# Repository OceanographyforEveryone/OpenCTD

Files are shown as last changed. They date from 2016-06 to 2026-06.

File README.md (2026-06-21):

# OpenCTD Rev8 is here!

**The ocean belongs to everyone.** The tools to study the ocean should be accessible to anyone with the curiosity and motivation to pursue that inquiry. Build your own [research-quality oceanographic instrument](https://tos.org/oceanography/article/the-openctd-a-low-cost-open-source-ctd-for-collecting-baseline-oceanographic-data-in-coastal-waters) and let's explore the ocean, together. 

# OpenCTD: Oceanography for Everyone

The CTD is an oveanographic instrument that measures salinity, temperature, and depth. By measuring these
characteristics, scientists can begin to unlock ocean patterns hidden beneath the sea's surface.

CTDs come in a variety of shapes, sizes, and applications. Most oceanographic research vessels have a CTD connected to a rosette platform, which houses other instruments and collects water samples in parallel with real-time data. CTDs are also commonly attached to fixed moorings, autonomous underwater vehicles (AUVs), remote-operated vehicles (ROVs), and even to marine animals.

Unfortunately, commercial CTDs are expensive. The most affordable models cost several thousand dollars. For near-shore oceanographic research on the relatively shallow continental shelf, this cost can be prohibitive. This
effectively excludes formal researchers from low and middle income countries, and small island states. Even in high-income countries, formal researchers at teaching institutions or at early career stages may also find themselves priced out of ocean research. Informal researchers such as citizen oceanographers, educators, conservation and management practitioners and students of all levels face severe challenges accessing expensive scientific instruments. 

**You don’t need to ask for permission to understand your world.**

By building your own instruments to study and understand the natural world, you are expanding the circle of knowledge production. A scientist who can make their own instruments is not beholden to the cycles of funding and access that constrain formal, institutional inquiry. A researcher who can build and repair their own equipment is not dependent on the whims of academic sentiment to decide what is and is not worthy of study. A community leader who has the tools to create their own data does not have to wait for institutions to take notice
of an emerging crisis before taking action. 

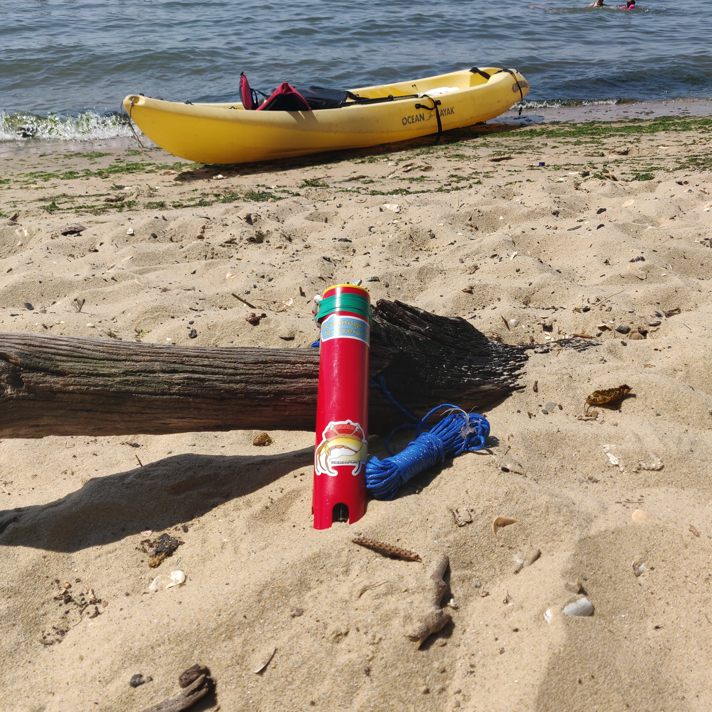
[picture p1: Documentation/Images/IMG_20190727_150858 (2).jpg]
The OpenCTD


### Build Your Own CTD

The OpenCTD is a low-cost, open-source CTD designed for budget-restricted
scientists, educators, and researchers working in nearshore coastal ecosystems.
In these waterways, entire research projects can be conducted for less than the
cost of a commercial CTD. OpenCTD was developed by a core team of marine
ecologists in collaboration with a community of scientists, engineers, makers,
and conservation practitioners from around the world. It is assembled from
components commonly available at large hardware stores or through major online
retailers. An Arduino-based microcontroller controls an array of sensors sealed
within a PVC pipe. Power is provided by a standard 3.7V lithium polymer battery
and data are stored in a tab-delimited text file accessed via SD card.  All
OpenCTD software is released open source with no restrictions on use. 

The OpenCTD built by the end-user, providing both access to
the tools of oceanography as well as the skills to maintain, repair, and
replace OpenCTDs. For scientists working in remote settings, the repairability
of the OpenCTD is intended to prevent equipment failures from spiraling into
project failures. For educators seeking novel, in-depth, hands-on STEM
experience for advanced students, the process of building an OpenCTD offers an
introduction to coding, 3D-printing, hardware prototyping, and electronics.
Construction of an OpenCTD can provide a practical foundation for courses in
oceanography and marine or environmental science. 

# Visit [Oceanography for Everyone](http://oceanographyforeveryone.com/) to learn more, inquire about workshops, or purchase OpenCTD kits!

### Publications

Thaler, A., S.K. Sturdivant, R.Y. Neches, and J.J. Levenson. 2024. [The OpenCTD: A low-cost, open-source CTD for collecting baseline oceanographic data in coastal waters](https://tos.org/oceanography/article/the-openctd-a-low-cost-open-source-ctd-for-collecting-baseline-oceanographic-data-in-coastal-waters#citation). Oceanography 37(2):167–173, https://doi.org/10.5670/oceanog.2024.602.

### Core Resources

The [OpenCTD Construction and
Operation](https://github.com/OceanographyforEveryone/OpenCTD/tree/main/Documentation)
manual provides a comprehensive, step-by-step guide to building your own
OpenCTD, with a standard construction pathway as well as numerous alternatives
depending on parts availability and technical skills. A shorter manual covering just the calibration process is also available. 

The OpenCTD [core software](https://github.com/OceanographyforEveryone/OpenCTD/tree/main/Software) is designed
to be used with an M0-style Arduino microcontroller, for which we recommend the
[Adafruit Adalogger Feather M0](https://www.adafruit.com/product/2796). 

You can find all the Arduino libraries as described in the manual, as well as
software for calibrating the conductivity sensors in
[Support](https://github.com/OceanographyforEveryone/OpenCTD/tree/main/Software/Support).

Hardware file for both 3D printable components and the control unit PBC can be found in [Hardware](https://github.com/OceanographyforEveryone/OpenCTD/tree/main/Hardware)

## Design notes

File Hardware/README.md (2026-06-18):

# OpenCTD Hardware 

This directory contains hardware files for building the OpenCTD Rev8. The [3D printable shapefiles](https://github.com/OceanographyforEveryone/OpenCTD/tree/main/Hardware/3DPrints) include the PowerSquid protective chassis, the sensor baseplate, and the router jigs and other accessories. The [printed circuit boards](https://github.com/OceanographyforEveryone/OpenCTD/tree/main/Hardware/PCB) include the KiCad and Gerber files for the OpenCTD Rev8 Control Board and the Oceanography for Everyone Custom Pressure Sensor breakout board. 

If you've been lucky enough to recieve Andrew's business card, [Benchtester](https://github.com/OceanographyforEveryone/OpenCTD/tree/main/Hardware/Benchtester) includes instructions for building a working test board for OpenCTD components, though, please note, the Benchtester was designed for the OpenCTD Rev7. 

### Electronics

The OpenCTD is controlled by an [Adalogger Feather M0](https://www.adafruit.com/product/2796) microcontroller development board.

Instructions on how to upload OpenCTD firmware to the microcontroller board can
be found in [Documentation](https://github.com/OceanographyforEveryone/OpenCTD/tree/main/Documentation). General instructions and
learning resources about the Adalogger Feather M0 board itself can be found in the [Adafruit Learning
Guide](https://learn.adafruit.com/adafruit-feather-m0-adalogger/).

The OpenCTD electronics can be assembled using a breadboard, or using a custom PCB. The custom PCB is designed using [KiCad](https://www.kicad.org/), and can be ordered in small batches from many PCB fabrication services around the world using the files located in the [PCB](https://github.com/OceanographyforEveryone/OpenCTD/tree/main/Hardware/PCB) directory.

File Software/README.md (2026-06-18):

# OpenCTD Software

This directory contains software for using the OpenCTD. There are three types of
software here: firmware, which runs on the OpenCTD itself; support software, which includes the require Arduino libraries as well as software for calibrating the conductivity sensor; and analysis
software, which is used to process data files copied from the OpenCTD to
another device (such as a personal computer) for analysis.

### Support Notes

Users may encounter the following issue: ["Code doesn't compile due to problem in RTCLib. Happens for both OpenCTD_mo.ino and RTC_Reset.ino"](https://github.com/OceanographyforEveryone/OpenCTD/issues/37) which can be solved by installing the library [Adafruit_BusIO](https://www.arduino.cc/reference/en/libraries/adafruit-busio/)

### Firmware

The OpenCTD is controlled by an [Adalogger Feather
M0](https://www.adafruit.com/product/2796) microcontroller development board.
Instructions on how to upload OpenCTD firmware to the microcontroller board can
be found in the [Documentation](https://github.com/OceanographyforEveryone/OpenCTD/tree/main/Documentation). General instructions and
learning resources about the Adalogger Feather M0 board itself can be found in
the [Adafruit Learning
Guide](https://learn.adafruit.com/adafruit-feather-m0-adalogger/).

[OpenCTD_m0_Rev8](https://github.com/OceanographyforEveryone/OpenCTD/tree/main/Software/Firmware/OpenCTD_m0_Rev8): This is the core software
for the OpenCTD. The file `OpenCTD_m0_Rev8.ino` contains the firmware
used in normal deployment of the OpenCTD instrument.

### Support
[Calibration](https://github.com/OceanographyforEveryone/OpenCTD/tree/main/Software/Support/Serial_for_EC_Calibration_m0): The calibration software which allows users to calibrate the Atlas Scientific EZO conductivity sensor.

[RTC Reset](https://github.com/OceanographyforEveryone/OpenCTD/tree/main/Software/Support/RTC_Reset): A small program to help you reset the real-time clock if it falls out of sync. 

[Arduino Libraries](https://github.com/OceanographyforEveryone/OpenCTD/tree/main/Software/Support/Arduino%20Libraries): Four Arduino Libraries required to run the OpenCTD, in downloadable ZIP files. 

### Analysis

OpenCTD writes data
to its microSD card in a generic CSV format that is compatible with many
different tools. In the [Analysis](https://github.com/OceanographyforEveryone/OpenCTD/tree/main/Software/Analysis) directory, you will find a few
examples of how to import and process data from the OpenCTD using different
software packages. Please use the software that best suits your own needs.

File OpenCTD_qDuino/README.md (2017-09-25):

OpenCTD Introduction and Build Guide
=======

*__Updated 9/25/2017__*

### 1.0 Overview

**Conductivity, temperature, and depth (CTD).**  These three measurements allow scientists to unlock ocean patterns hidden beneath the sea's surface. The ocean is not uniform, it its filled with swirling eddies, temperature boundaries, layers of high and low salinity, changing densities, and other physical characteristics invisible to an observer floating upon its surface. To reveal these patterns oceanographers employ the CTD--an oceanographic instrument that, at its core, measures temperature, salinity, and depth for a water column. The CTD is the workhorse of oceanographic research. 

CTDs are expensive, and that expense can is a barrier-to-entry for formal and informal researchers with limited budgets, scientists from developing nations, citizen oceanographers, and students of all levels interested in learning more about their local coasts and waterways. 

The OpenCTD is a low-cost, open-source CTD suitable for both educators and researchers. The platform is built using reasonably accessible parts and is powered by an Arduino-based microcontroller. Source codes and building instructions are freely available. The device, sufficiently accurate for scientific research, can be constructed for approximately $300, and is effective to 100 meters depth.

Why 100 meters? For many coastal regions, 100 meters depth covers the majority of the ocean that is accessible by small boat and generally the average depth of the outer continental shelf. The OpenCTD is targeted to people working in this niche, where entire research projects can be conducted for less than the cost of a commercial CTD. The OpenCTD is scalable and someone with the inclination and expertise can adapt an OpenCTD to operate in deeper waters.

*__If you build an OpenCTD please let the [team at Oceanography For Everyone](http://oceanographyforeveryone.com/#meetAnchor) know. We love to keep up with the community of people building and using these devices. During your build session, or while using an OpenCTD or other [Oceanography for Everyone](http://oceanographyforeveryone.com/) tools, please consider tweeting using the [#HackTheOcean](https://twitter.com/hashtag/HackTheOcean?src=hash) hashtag so the community can follow your efforts!__*

#### 1.1 Skills Needed

Building an OpenCTD requires some basic soldering and coding knowledge but it is also a great opportunity to learn those skills. With an hour or two of practice, you can develop the soldering skills needed to build an OpenCTD. [This descriptive, illustrative comic from Mighty Ohm](http://mightyohm.com/files/soldercomic/FullSolderComic_EN.pdf) presents soldering fundamentals in an accesible and approachable format.

Andrew has used this [MightyOhn Geiger Counter Kit](http://mightyohm.com/blog/products/geiger-counter/) and this [Mega Menorah 9000 Soldering Kit](http://shop.evilmadscientist.com/productsmenu/756) to teach soldering and basic electronic principles to students from ages 10 to 65. 

Arduino is a relatively intuitive coding environment, but it can still seem daunting to first-time users. Practically, we have already created the code you will need to run the OpenCTD, but it is extremely beneficial, particularly for end users, to understand what the software is doing. The book [Environmental Monitoring with Arduino: Building Simple Devices to Collect Data About the World Around Us](http://amzn.to/2xB15Xi) is short, easy to understand, and will provide you with some ideas for expanding your inventory of open-source environmental sensors. 

### 2.0 Project Status

The OpenCTD is stable on the Qduino Mini platform with comprehensive build instructions provided and a growing user community. We have validated the OpenCTD against commercial CTDs and are confident in the quality of the data. Users around the world are building and testing their own units and helping with instrument validation.  

#### 2.1 Field Trials

As we test and refine the design of the OpenCTD, critical field trials with essential data for assessing the quality, accuracy, and durability of the device are archived in the [Field_Trials](https://github.com/OceanographyforEveryone/OpenCTD/tree/master/Field_Trials) repository.

+ **_Lake Superior, R/V Blue Heron_:** Initial field trials were completed in October of 2015 and analysis of the data from the first several casts confirms the accuracy of OpenCTD at it was cast against a commercial CTD. Additionaly, OpenCTD was successfully deployed to a depth of 140 meters. All data and field notes from the first Field Trial can be found in the [Blue Heron 15-11](https://github.com/OceanographyforEveryone/OpenCTD/tree/master/Field_Trials/Blue_Heron_2015-11) repository.

+ **_Gloucester Point, VA, Hurricane Hermine_:** Hurricane Hermine is a tropical cyclone that passed over our field site in coastal Virginia on September 4, 2016. To test the longevity of the batteries and the durability of the OpenCTD during long term deployments, Andrew placed two units in our Test Ditch (a tidally influence drainage ditch connected to the Mobjack Bay estuary), where they remained for 74 hours. Notes and data files can be found in the [HermineDeployment_9-2016](https://github.com/OceanographyforEveryone/OpenCTD/tree/master/Field_Trials/HermineDeployment_9-2016) respository.

### 3.0 Bill of Materials

We try to source as many parts as possible from accesible distibutors. **_NOTE: As Amazon is in the process of phasing out its aStore program, the Parts Depot is no longer being maintained. Please consult the below list for the most recent part recommendations._** Many components can also be purchased directly through the supplier, found on AliExpress, or sourced through auction sites for significantly less. Quality across suppliers for most parts has been generally consistent, though we have noticed a defect rate of about 10% with the sealed temperature sensors. 

**Please be aware: Part availability varies from month to month, and some components may become permanently unavailble or listed under a new manufacturer and product name. We do our best to keep the bill of material up to date, If you find any discrepancies, please email us.**

**Recommended Components**

Part	| Suplier	| Price	| Link	
---|---|---|---
Qduino Mini |	Sparkfun/Amazon	| $29.95	| https://www.sparkfun.com/products/13614	/ http://amzn.to/2wS8YUp
SD Card Reader Module	|  Amazon	| $5.66	| http://amzn.to/2jXSNnv 	
3.7V 2000mAh LiPo	| Amazon	| $14.98	| http://amzn.to/2y3nDRQ						
Conductivity K 1.0 Kit |	Atlas Scientific  |	$195.71	| https://www.atlas-scientific.com/product_pages/kits/ec_k1_0_kit.html	
DS18B20 Temperature Sensor | Amazon | $9.88 |	http://amzn.to/2yoBUo6				
MS5803-14BA	|	Mouser	| $22.85	| http://www.mouser.com/ProductDetail/Measurement-Specialties/MS580314BA01-00
SOIC to DIP Adapter	|	Sparkfun	| $2.95	| https://www.sparkfun.com/products/13655
0.1uF Capacitor	| Amazon	| $4.79	| http://amzn.to/2humBn9
10k Ohm Resistor	|	Amazon	| $4.19	| http://amzn.to/2yoCjqC	
4.7kOhm Resistor | Amazon	| $6.16	| http://amzn.to/2fMfmHe					
Hook-up wire	|	Amazon	| $22.00	| http://amzn.to/2hu54eJ	
Heat shrink tubing |	Amazon	| $5.99	|http://amzn.to/2wRQtPO	
2" Gripper Plug | Amazon | $9.41 | http://amzn.to/2jWVjdz

**Alternate Components**

Part	| Suplier	| Price	| Link	
---|---|---|---
MicroSD Card Read Module	|  Amazon	| $9.49	| http://amzn.to/2y4nSvS
Pressure Sensor Breakout - MS5803-14BA | SparkFun | $59.95 | https://www.sparkfun.com/products/12909
3" Gripper Plug | Amazon | $4.99 | http://amzn.to/2wS9qlC

**Some parts, such as resistors and capacitors, are very cheap but hard to source individually. We have tried to find the smallest lots that aren't excessively overpriced, but you may have better luck finding cheaper options, especially "intro to electronics"-type kits, which include many standard resistors and capacitors in small lots.** 

Additional components, like a pre-fabricated [pressure sensor module](https://www.sparkfun.com/products/12909), [LiPo batteries](https://www.sparkfun.com/products/8483), [SMD boards](https://www.sparkfun.com/products/13655), and the [qDuino Mini](https://www.sparkfun.com/products/13614) can be found at Sparkfun. The MS5803-14BA pressure sensor previously needed to be special ordered from a parts supplier, but [SparkFun](https://www.sparkfun.com/products/12909) has a (much more expensive) commercial 14-bar unit using the same sensor. 

Servoflo sells the raw, calibrated pressure sensor in both [14Bar](http://www.servoflo.com/download-archive/data-sheets/220-calibrated-digital-sensor-modules/614-ms5803-14ba) and [30Bar](http://www.servoflo.com/download-archive/data-sheets/220-calibrated-digital-sensor-modules/613-ms5803-30ba) modules. These are surface mounted sensors and require significant soldering skills to mount properly. Detailed descriptions of the differeces and benefits between the two pressure sensors is discussed in section 5.2. Mouser now sells individual MS5803-14BA sensor modules for a reasonable cost.

PVC pipe can be found at most home supply stores. If you want to get fancy, a [clear acrylic tube](http://amzn.to/2njFhqw) can add some flare to your build. Though the first OpenCTDs were built using 3" PVC pipe, we now recommend using 2" pipe for a more durable, compact device.

#### 3.1 Tools
- wire cutter
- wire stripper
- soldering iron
- solder tip cleaner
- helping hands soldering station
- epoxy gun
- needle-nosed pliers
- multimeter
- utility knife
- hot glue gun
- heat gun
- saw
- drill
- 1" bit (for holes in PVC)
- laptop
- micro-USB cable
- coffee maker (because coffee)

#### 3.2 Consumables
- sand paper
- Hysol E90-FL epoxy
- venturi mixing nozzles for epoxy
- solder
- desoldering braid
- electical tape
- hot glue
- mineral oil
- calibration standard for conductivity
- coffee

#### 3.3 3D printed parts
Several useful parts that will significantly improve the build process are 3D printable: [3D Printer Files](https://github.com/OceanographyforEveryone/OpenCTD/tree/master/3D_Printer_Files). While 3D printing allows rapid fabricating of small custom parts for very low cost, we recognize that access to a 3D printer is not universal. The OpenCTD can be entirely constructed without 3D printed parts. The sensor plate can be fabricated from cardboard if necessary (its purpose is to hold the sensors in place while the expoxy cures, once the epoxy is set, the plate serves no further function). The wire jig helps keep everything organized but is not necessary. The Jaunty CTD Cap is funny, but not particularly useful. If you would like to build an OpenCTD but do not have access to a 3D printer, please contact either Andrew or Russell and we will print the parts for you. If you're on [Thingiverse](https://www.thingiverse.com/), please Like, Collect, or Make our designs to help boost our profile in the 3D-printing community. 

+ [OpenCTD sensor template](https://www.thingiverse.com/thing:1641934)
+ [OpenCTD hardware frame and wire guide](https://www.thingiverse.com/thing:2500591)
+ [Jaunty Red Cap for the OpenCTD](https://www.thingiverse.com/thing:2470929)

#### 3.4 Required Arduino Libraries
+ Included with Arduino IDE:
  - [**SPI.**](https://www.arduino.cc/en/Reference/SPI) Serial Peripheral Interface for communicating with a standard SD card reader.
  - [**SoftwareSerial.**](https://www.arduino.cc/en/Reference/SoftwareSerial) For communicating with serial devices like the conductivity circuit.
  - [**Wire.**](https://www.arduino.cc/en/Reference/Wire) For communicating with I2C devices like the pressure sensor. 
+ Need to download and install ([How to install Arduino libraries](https://www.arduino.cc/en/Guide/Libraries)):
  + [**SD.**](https://www.arduino.cc/en/Reference/SD) For reading and writing to a standard SD card reader.
  + [**SparkFun_MS5803_I2C.**](https://github.com/sparkfun/SparkFun_MS5803-14BA_Breakout_Arduino_Library/tree/V_1.1.0) For the MS5803 14 Bar pressure sensor (*__Note__: if you decide to use a different pressure sensor, you will need to update this library*)
  + [**Dallas Temperature Control.**](https://milesburton.com/Dallas_Temperature_Control_Library) Allows you to communicate with the DS18B20 thermistor. 
  + [**OneWire.**](http://www.pjrc.com/teensy/td_libs_OneWire.html) For controlling the Dallas 1-wire family of devices. 

#### 3.5 Other Useful Software

+ [**Qduino.h and Qduino fuelGauge**](https://github.com/sparkfun/Arduino_Boards/tree/master/sparkfun/avr/libraries/Qduino) allows you to measure the charge on you battery. 
+ [**simple_serial_for_EC_calibration**](https://github.com/OceanographyforEveryone/OpenCTD/tree/master/Support_Code/simple_serial_for_EC_calibration) is a basic serial monitor program to help you calibrate the conductivity probe. 
+ [**TempProbeTester**](https://github.com/OceanographyforEveryone/OpenCTD/tree/master/Support_Code/TempProbeTester) allows you to test up to 26 temperature probes simultaneously and is useful for quality control and temperature calibrations. 
+ [**MS5803_14_test**](https://github.com/OceanographyforEveryone/OpenCTD/tree/master/Support_Code/MS5803_14_test) For testing the pressure sensor prior to installation. 

### 4.0 Arduino Qduino Pinouts

- **SD Card Reader:** CS (D4), SCK (D15), MOSI (D16), MISO (D14*)
- **Pressure Sensor:** SDA (D2), SCL (D3)
- **Temperature Sensors:** Data (D6)
- **Conductivity Circuit:** TX (D8), RX (D9)

\*older Qduinos may have this labeled D17

**It is possible to use other Arduino-based single board computers, but please check the pinouts and schematics. Different Arduino boards may use various pins for internal functions which can interfere with signals to and from the sensors (for example, using this pinout on an Arduino Uno will result in failed conductivity readings).**

### 5.0 Build Instructions

*We are continously updating and improving OpenCTD prototypes. These instuctions are subject to change. Please read through the entire guide before you make any irreversible changes to the hardware. Most manufacturers will consider the warranty void once you begin soldering.*

**Important note about power consumption:** All sourced modules are rated to work at 3.3V, however, when two or more are running simultaneously, the 3.3V output on most Arduinos yield inconsistent results and the SD card reader may not function at all. We recommend powering the entire system with a minimum of 3.7V. On standard Arduino's, the 5V output should be used. On the Qduino Mini, VCC with a 3.7V battery is sufficient. **_You can save yourself a lot of headache if you make sure the LiPo battery is fully charged and leave it connected to the Qduino Mini throughout the build._**

**_We strongly encourage you to test all the components one by one on a breadboard before soldering modules together. If you're planning to build multiple CTDs, we recommend that you use a dedicated Qduino, with header pins, for breadboard testing._**

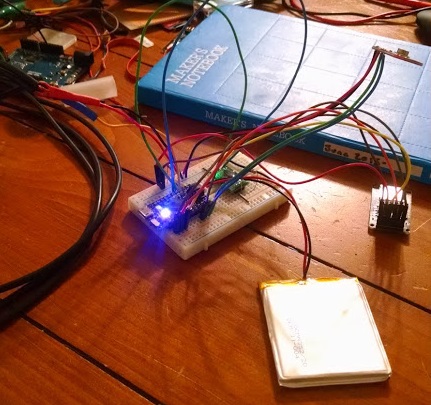
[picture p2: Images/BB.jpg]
A complete OpenCTD system mounted to a breadboard for testing before soldering and potting
&nbsp;&nbsp;&nbsp;&nbsp;&nbsp;&nbsp;&nbsp;&nbsp;&nbsp;&nbsp;&nbsp;&nbsp;

&nbsp;&nbsp;&nbsp;&nbsp;&nbsp;&nbsp;&nbsp;&nbsp;&nbsp;&nbsp;&nbsp;&nbsp;*A complete OpenCTD system mounted to a breadboard for testing before soldering and potting.*

Before you begin, set up you Qduino Mini following this [helpful quickstart guide from Qtechknow](https://www.hackster.io/team-qtechknow/qduino-mini-quickstart-guide-8b2d68) and flash the [OpenCTD software](https://github.com/OceanographyforEveryone/OpenCTD/tree/master/OpenCTD_qDuino) to your Qduino Mini so that you can test each component during the build.

#### 5.1 SD Card Reader

The [SD card reader](http://amzn.to/2xEPbM9) we recommend is a 'plug and play' module. Connect each pin following the pinout guide above. For fitting into a tight housing, you may want to bend each header pin 90 degrees (using needle-nosed pliers) or remove the headers completely. Hookup wires should be at least 60 mm long, though you may eventually shorten them to suit your preference. For SD card readers with two sets of pins, bend the 6 pins you need 90 degrees and snip the others flush with the board. Make sure you're connecting to the 3.3V terminal, not the 5V terminal. 

To prepare the SD card, format the card and create a single, empty text file called **datalog.txt**.

#### 5.2 Pressure Sensor

There are several options and configurations for the pressure sensor, all of which rely on the MS5803-14BA sensor module. The simplest solution is a prefabricated model that requires no additional modificaion, just solder headers or connectors to Gound, Vin, SCL, and SDA and connect to the Qduino (we strongly recommend this option for people who do not have extensive experience with surface mounted soldering). 

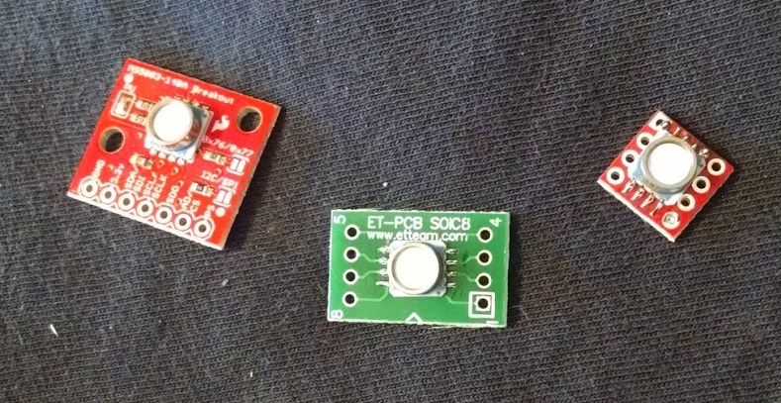
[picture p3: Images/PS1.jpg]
Three possible pressure modules. Three possible pressure modules
&nbsp;&nbsp;&nbsp;&nbsp;&nbsp;&nbsp;&nbsp;&nbsp;&nbsp;&nbsp;&nbsp;&nbsp;

&nbsp;&nbsp;&nbsp;&nbsp;&nbsp;&nbsp;&nbsp;&nbsp;&nbsp;&nbsp;&nbsp;&nbsp;*Three possible pressure modules.*

Other solutions require a small 100nF (104) capacitor and 10kOhm pull-up resistor. The resistor bridges pin 3 and 6 on the pressure module. The capacitor bridges pins 2 and 5. SCLK is pin 1, Ground is pin 2, VCC in pin 5, and SDI/SDA is pin 7. Pins 5 and 6 need to be bridged with a jumper wire. 

&nbsp;&nbsp;&nbsp;&nbsp;&nbsp;&nbsp;&nbsp;&nbsp;&nbsp;&nbsp;&nbsp;&nbsp;Layout for pressure module

&nbsp;&nbsp;&nbsp;&nbsp;&nbsp;&nbsp;&nbsp;&nbsp;&nbsp;&nbsp;&nbsp;&nbsp;*Layout for pressure module. From [The Cave Pearl Project](https://edwardmallon.wordpress.com/2014/03/27/adding-a-ms5803-02-high-resolution-pressure-sensor/).*

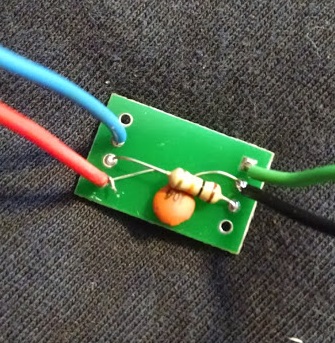
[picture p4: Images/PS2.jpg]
Back view of one DIY pressure module Back view of one DIYpressure module
&nbsp;&nbsp;&nbsp;&nbsp;&nbsp;&nbsp;&nbsp;&nbsp;&nbsp;&nbsp;&nbsp;&nbsp;

&nbsp;&nbsp;&nbsp;&nbsp;&nbsp;&nbsp;&nbsp;&nbsp;&nbsp;&nbsp;&nbsp;&nbsp;*Back view of one DIY pressure module.*

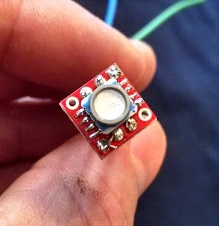
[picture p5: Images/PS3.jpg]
Front view of a small DIY pressure module
&nbsp;&nbsp;&nbsp;&nbsp;&nbsp;&nbsp;&nbsp;&nbsp;&nbsp;&nbsp;&nbsp;&nbsp;

&nbsp;&nbsp;&nbsp;&nbsp;&nbsp;&nbsp;&nbsp;&nbsp;&nbsp;&nbsp;&nbsp;&nbsp;*Front view of a small DIY pressure module.*

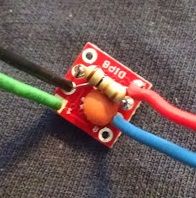
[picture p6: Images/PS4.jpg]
Back view of the same DIY pressure module
&nbsp;&nbsp;&nbsp;&nbsp;&nbsp;&nbsp;&nbsp;&nbsp;&nbsp;&nbsp;&nbsp;&nbsp;

&nbsp;&nbsp;&nbsp;&nbsp;&nbsp;&nbsp;&nbsp;&nbsp;&nbsp;&nbsp;&nbsp;&nbsp;*Back view of the same DIY pressure module.*

Hookup wires for the pressure sensor should be about 5 cm longer than the length of pipe used for the housing. You may end up shortening these depending on your preference. The [MS5803_14_test](https://github.com/OceanographyforEveryone/OpenCTD/tree/master/Support_Code/MS5803_14_test) code can be used to test the pressure sensor after assembly.

#### 5.3 Temperature Sensors

The temperature probes use an off-the-shelf DS18B20 digital thermistor in a stainless steel housing. We use a battery of 3 probes averaged together for more consistent readings. The OneWire protocol allows mutliple probes to be queried on the same pin, so all three probes feed into a single data pin. With these low-cost thermistors, we've found the failure rate to be about 10% out of the box. It's worth testing each thermistor on a breadboard before proceeding to save yourself frustration down the line. To prepare the probes, cut the wire length to 30 cm. Solder three data strands, three power strands, and three ground strands together and attach a single solid core wire to each. 

We recommend sealing each solder joint with waterproof heat shrink tubing for increased reliability and to protect connections in the event of a flooded housing. 

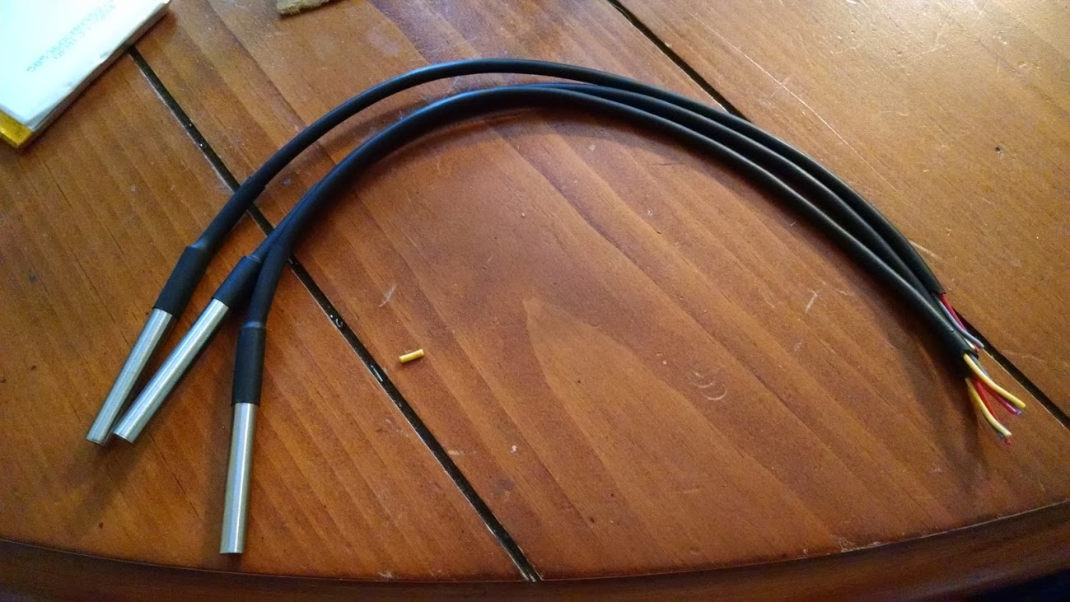
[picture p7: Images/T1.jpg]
Three temperature probes prepped for soldering Three termperature probes prepped for soldering
&nbsp;&nbsp;&nbsp;&nbsp;&nbsp;&nbsp;&nbsp;&nbsp;&nbsp;&nbsp;&nbsp;&nbsp;

&nbsp;&nbsp;&nbsp;&nbsp;&nbsp;&nbsp;&nbsp;&nbsp;&nbsp;&nbsp;&nbsp;&nbsp;*Three temperature probes prepped for soldering.*

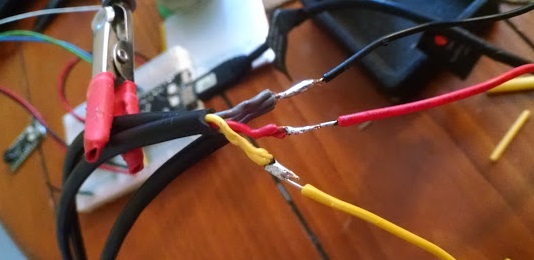
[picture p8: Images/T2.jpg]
Temperature probes connected
&nbsp;&nbsp;&nbsp;&nbsp;&nbsp;&nbsp;&nbsp;&nbsp;&nbsp;&nbsp;&nbsp;&nbsp;

&nbsp;&nbsp;&nbsp;&nbsp;&nbsp;&nbsp;&nbsp;&nbsp;&nbsp;&nbsp;&nbsp;&nbsp;*Temperature probes connected.*

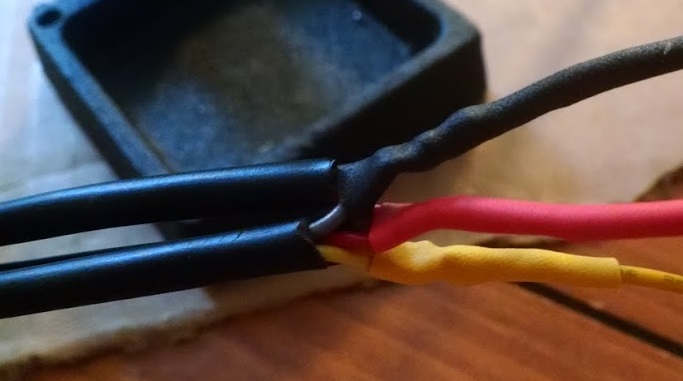
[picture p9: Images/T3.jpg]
Temperature probes treated with heat shrink
&nbsp;&nbsp;&nbsp;&nbsp;&nbsp;&nbsp;&nbsp;&nbsp;&nbsp;&nbsp;&nbsp;&nbsp;

&nbsp;&nbsp;&nbsp;&nbsp;&nbsp;&nbsp;&nbsp;&nbsp;&nbsp;&nbsp;&nbsp;&nbsp;*Temperature probes treated with heat shrink.*

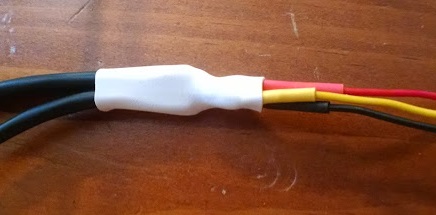
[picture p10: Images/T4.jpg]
Temperature probes treated with additional heat shrink to keep everything tindy Temperature probes treated with additional heat shrink.
&nbsp;&nbsp;&nbsp;&nbsp;&nbsp;&nbsp;&nbsp;&nbsp;&nbsp;&nbsp;&nbsp;&nbsp;

&nbsp;&nbsp;&nbsp;&nbsp;&nbsp;&nbsp;&nbsp;&nbsp;&nbsp;&nbsp;&nbsp;&nbsp;*Temperature probes treated with additional heat shrink.*

Finally, you will need to bridge the Vcc and Data pin (Vcc and D6 on the Qduino) with a 4.7 kOhm pull-up resisitor. This should be done when you solder everything directly to the Arduino. 

#### 5.4 Conductivity Sensor

There are a variety of options for conductivity probes, but we recommend using the [Atlas EC EZO circuit](http://www.atlas-scientific.com/product_pages/circuits/ezo_ec.html) to drive these probes. Different conductivity probes will have different configurations. In many cases, there will be more wires than are used. Use a multimeter to trace which wires are actually connected to each electrode. Once you have the electrodes traced, cut the wire to approximately 25cm and set the probe aside for potting. 

The Atlas conductivity circuit needs very little preparation. Solder hook-up wires to all contacts except the two probe contacts. The conductivity probe will eventually be attached to these. 

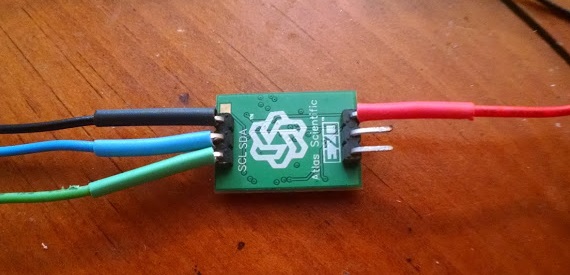
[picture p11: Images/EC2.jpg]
Conductivity circuit with heat-shrink to protect contacts
&nbsp;&nbsp;&nbsp;&nbsp;&nbsp;&nbsp;&nbsp;&nbsp;&nbsp;&nbsp;&nbsp;&nbsp;

&nbsp;&nbsp;&nbsp;&nbsp;&nbsp;&nbsp;&nbsp;&nbsp;&nbsp;&nbsp;&nbsp;&nbsp;*Conductivity circuit with heat-shrink to protect contacts.*

#### 5.5 Prepare the housing.

Cut a 2" PVC pipe to 25 cm in length. At one end of the pipe drill 2 equidistant holes to allow water flow around the sensors. The center of each hole should be 2.5 cm from the bottom edge. The position of the holes does not need to be precise, and you can get creative with their placement, provided you leave enough room for the sensor plate to sit above the holes. 

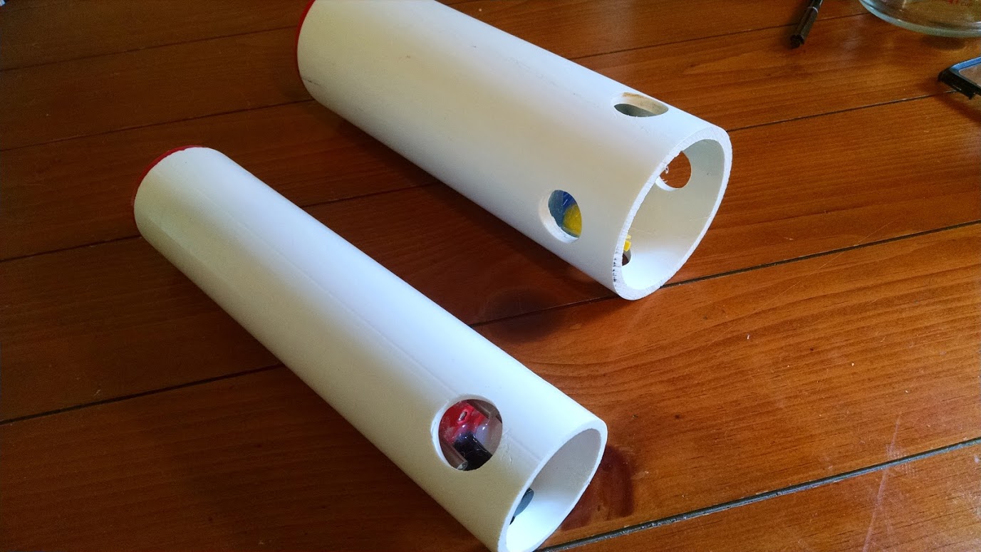
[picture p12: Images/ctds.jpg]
2 inch and 3inch OpenCTDs highlighting position of flow-through holes and probes 2 inch and 3 inch OpenCTDs highlighting position of flow-through holes and probes
&nbsp;&nbsp;&nbsp;&nbsp;&nbsp;&nbsp;&nbsp;&nbsp;&nbsp;&nbsp;&nbsp;&nbsp;

&nbsp;&nbsp;&nbsp;&nbsp;&nbsp;&nbsp;&nbsp;&nbsp;&nbsp;&nbsp;&nbsp;&nbsp;*2" and 3" OpenCTDs highlighting position of flow-through holes and probes* 

####  5.6 Connecting the electronics.

The 3D printed hardware frame and wire guide will make it easier to produce a nice, clean, easy to access brain for your open CTD. Each space is designed to hold one of the three PCB components, with the SD card reader located at the top, the qDuino mini in the middle, and the conductivity circuit on the bottom. The d-loop allows for wire routing using zipties to lock wire in place and take strain off of solder joints. 

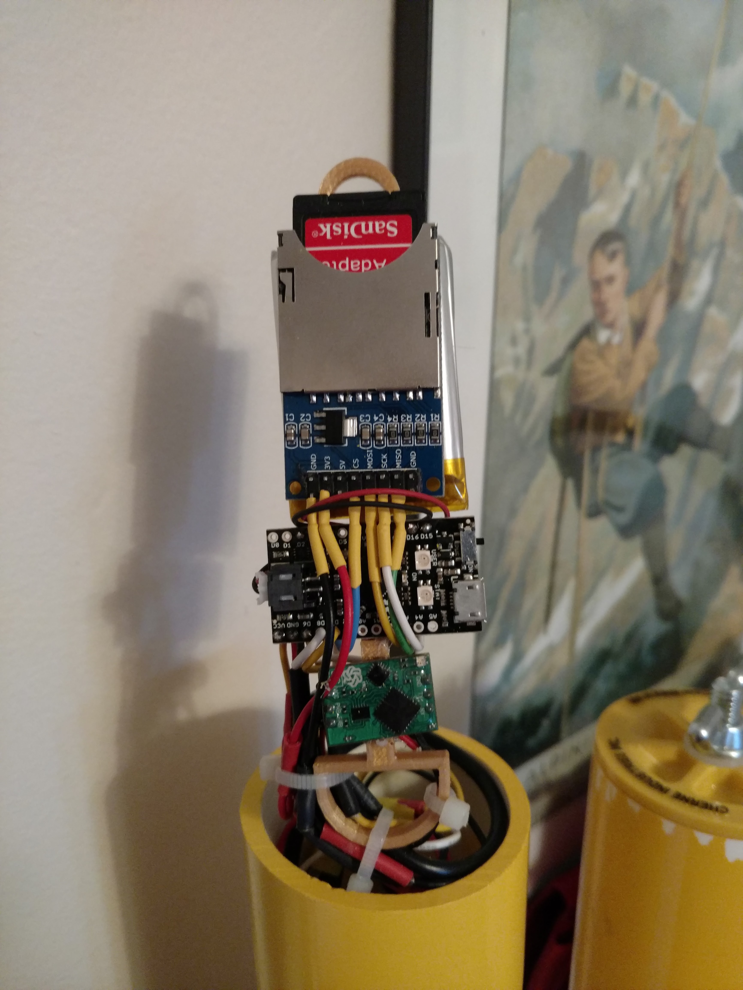
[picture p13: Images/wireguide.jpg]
OpenCTD hardware frame and wire guide.
&nbsp;&nbsp;&nbsp;&nbsp;&nbsp;&nbsp;&nbsp;&nbsp;&nbsp;&nbsp;&nbsp;&nbsp;

&nbsp;&nbsp;&nbsp;&nbsp;&nbsp;&nbsp;&nbsp;&nbsp;&nbsp;&nbsp;&nbsp;&nbsp;*OpenCTD hardware frame and wire guide.*

**Note:** Please test all electronics on a breadboard before permanently soldering to the Qduino. 

**Note:** Depending on how tight your OpenCTD housing is, you may want to pot the probes first, and then connect them. 

Create a power bus by soldering the four Vcc wires from each component to a single solid core wire so that they can all be connected to a single Vcc pin. Do the same with ground wires. Cover the connections with heat-shrink tubing. 

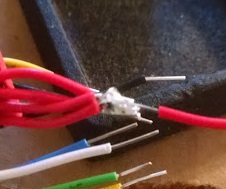
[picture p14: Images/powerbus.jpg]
Power bus, without heatshrink Powerbus, without heatshrink
&nbsp;&nbsp;&nbsp;&nbsp;&nbsp;&nbsp;&nbsp;&nbsp;&nbsp;&nbsp;&nbsp;&nbsp;

&nbsp;&nbsp;&nbsp;&nbsp;&nbsp;&nbsp;&nbsp;&nbsp;&nbsp;&nbsp;&nbsp;&nbsp;*Power bus, without heatshrink.*

Slot a 4.7 kOhm pullup resistor between Vcc and D6. Feed the Vcc and Ground power buses into their corresponding pinouts. Feed to temperature probe data connection into pin D6. With the pullup resistor, D6 and Vcc may be a tight fit. Solder all three pins. 

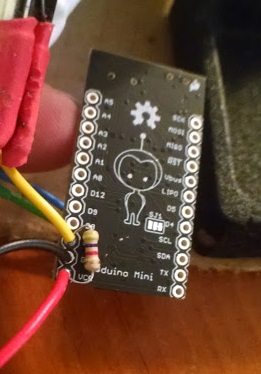
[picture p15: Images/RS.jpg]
Vcc, Ground, and D6 with pullup resistor
&nbsp;&nbsp;&nbsp;&nbsp;&nbsp;&nbsp;&nbsp;&nbsp;&nbsp;&nbsp;&nbsp;&nbsp;

&nbsp;&nbsp;&nbsp;&nbsp;&nbsp;&nbsp;&nbsp;&nbsp;&nbsp;&nbsp;&nbsp;&nbsp;*Vcc, Ground, and D6 with pullup resistor*

Solder the SD card reader and pressure sensor to the Qduino Mini following the [pinout guide](https://github.com/OceanographyforEveryone/OpenCTD/blob/master/README.md#40-arduino-qduino-pinouts). Solder the conductivity probe to the PRB headers on the Atlas circuit, then connect the Atlas circruit to the Qduino Mini following the [pinout guide](https://github.com/OceanographyforEveryone/OpenCTD/blob/master/README.md#40-arduino-qduino-pinouts). 

Depending on the size of the housing and how much wire you used in your build, fitting all of the electronics into the housing may require some creative placement. 

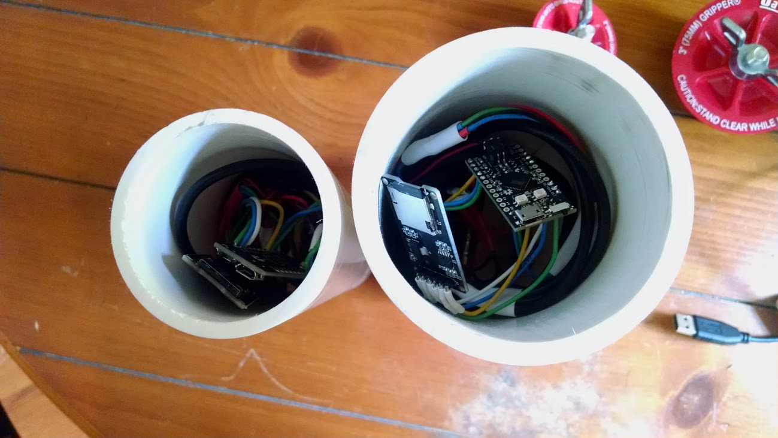
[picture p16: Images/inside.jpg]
2-inch and 3-inch OpenCTDs, highlighing electronics placement in the housing
&nbsp;&nbsp;&nbsp;&nbsp;&nbsp;&nbsp;&nbsp;&nbsp;&nbsp;&nbsp;&nbsp;&nbsp;

&nbsp;&nbsp;&nbsp;&nbsp;&nbsp;&nbsp;&nbsp;&nbsp;&nbsp;&nbsp;&nbsp;&nbsp;*2-inch and 3-inch OpenCTDs, highlighing electronics placement in the housing*

#### 5.8 Potting

*__This is the point of no return, after this step, there's no going back!__*

**Note:** Depending on how tight your OpenCTD housing is, you may want to pot the probes first, and then connect them. 

3D print the [OpenCTD baseplate](https://github.com/OceanographyforEveryone/OpenCTD/blob/master/3D_Printer_Files/OpenCTD_2in.stl). The outside of the baseplate is the portion of the base plate that will be exposed to the water--this is the side w/o the indentation for the pressure sensor.
 
Place a small amount of heatshrink tubing on the pressure sensor to prevent epoxy from coming in contact with the membrane. Affix the pressure sensor to the center indentation in the base plate. Lightly cover the edge of the indentation with 2-ton epoxy, taking care not to let any come in contact with the membrane. Seat the sensor in the indentation and apply more epoxy (This will provide added protection for this circuit). Let the epoxy cure for 20 minutes. Trim away the exposed heat shrink taking care not to damage the pressure sensor. **Optional: Apply a small amount of electrical tape over the membrane of the pressure sensor to protect it while you work.**
 
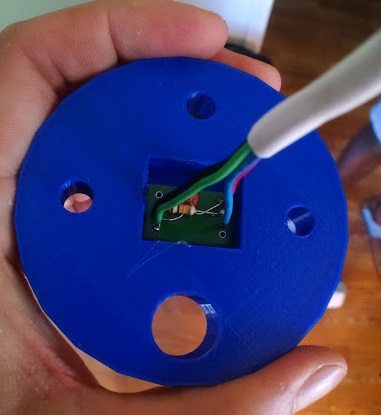
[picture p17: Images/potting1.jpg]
Pressure sensor seated in the baseplate Pressure sensor seated in baseplate
&nbsp;&nbsp;&nbsp;&nbsp;&nbsp;&nbsp;&nbsp;&nbsp;&nbsp;&nbsp;&nbsp;&nbsp;
 
&nbsp;&nbsp;&nbsp;&nbsp;&nbsp;&nbsp;&nbsp;&nbsp;&nbsp;&nbsp;&nbsp;&nbsp;*Pressure sensor seated in baseplate.*

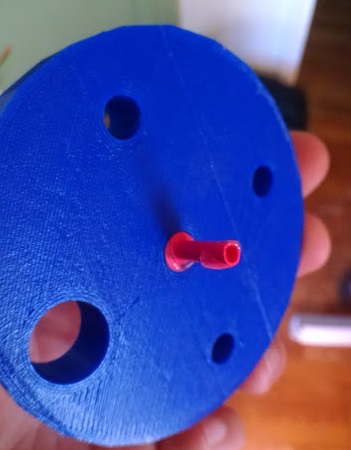
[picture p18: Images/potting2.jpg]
Pressure sensor with heat shrink extending out through baseplate
&nbsp;&nbsp;&nbsp;&nbsp;&nbsp;&nbsp;&nbsp;&nbsp;&nbsp;&nbsp;&nbsp;&nbsp;

&nbsp;&nbsp;&nbsp;&nbsp;&nbsp;&nbsp;&nbsp;&nbsp;&nbsp;&nbsp;&nbsp;&nbsp;*Pressure sensor with heat shrink extending out through baseplate.*
 
Place the three temperature sensors into the 3 small holes. The waterproofing around these probes is not always uniform. Make sure that some stainless steel is exposed on the inside surface of the baseplate and than at least 1 cm extends out into the water.
 
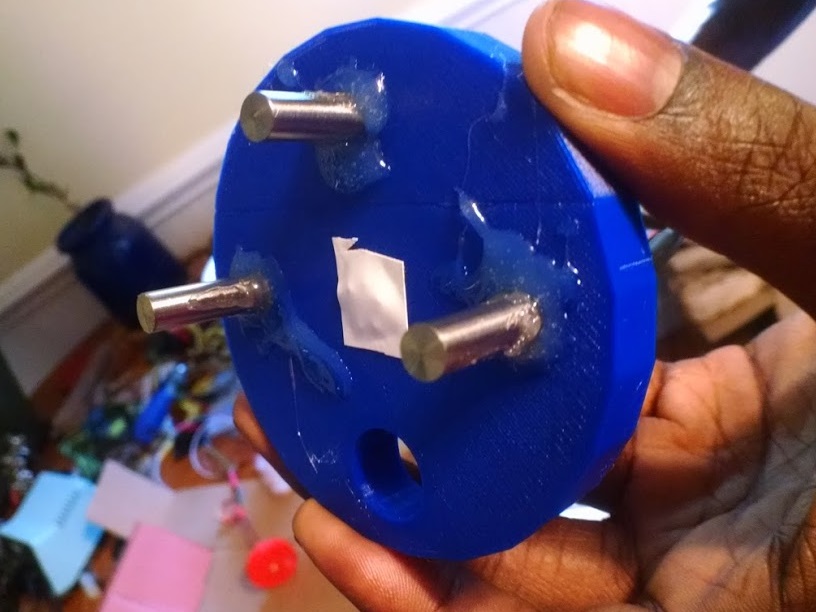
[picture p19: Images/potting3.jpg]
Temperature probes extending out through the baseplate Temperature probes extaneding out through the baseplate
&nbsp;&nbsp;&nbsp;&nbsp;&nbsp;&nbsp;&nbsp;&nbsp;&nbsp;&nbsp;&nbsp;&nbsp;
 
&nbsp;&nbsp;&nbsp;&nbsp;&nbsp;&nbsp;&nbsp;&nbsp;&nbsp;&nbsp;&nbsp;&nbsp;*Temperature probes extending out through the baseplate.*
 
Apply hot glue around the inside of the base plate around each temperature sensor to hold them in place and prevent epoxy from leaking out. Once the hot glue hardens, place the conductivity probe in the only hole big enough for it. Make sure the conductivity probe extends further from the baseplate than the temperature probes (to avoid any interference from these metal probes). Apply hot glue to the inside of the base plate around the conductivity sensor.
 
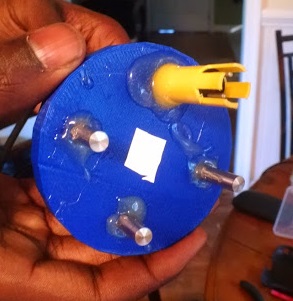
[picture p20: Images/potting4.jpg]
All probes extending out through the baseplate
&nbsp;&nbsp;&nbsp;&nbsp;&nbsp;&nbsp;&nbsp;&nbsp;&nbsp;&nbsp;&nbsp;&nbsp;
 
&nbsp;&nbsp;&nbsp;&nbsp;&nbsp;&nbsp;&nbsp;&nbsp;&nbsp;&nbsp;&nbsp;&nbsp;*All probes extending out through the baseplate.*
 
Align the baseplate such that it is lightly recessed into the tube (when standing upright [i.e. sensors facing down], none of the sensors should touch the ground) and that it sits just above the top of each flow-through hole. Remove the baseplate and apply hot glue around the edges of the plate. Quickly and carefully slide the plate back into the PVC pie while slowly rotating it. This will create a tight seal to prevent epoxy from leaking out.
 
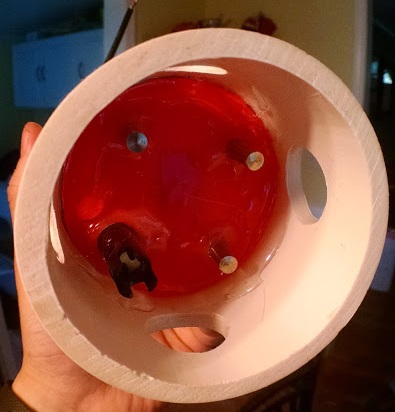
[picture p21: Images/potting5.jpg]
Baseplate seated in the housing
 &nbsp;&nbsp;&nbsp;&nbsp;&nbsp;&nbsp;&nbsp;&nbsp;&nbsp;&nbsp;&nbsp;&nbsp; 
 
 &nbsp;&nbsp;&nbsp;&nbsp;&nbsp;&nbsp;&nbsp;&nbsp;&nbsp;&nbsp;&nbsp;&nbsp;*Baseplate seated in the housing.*

Once you are satisfied with everything's position, it's time for EFL-90 epoxy. Using the epoxy gun apply the epoxy on the inside of the tube around the sensors. We recommend using an entire cartridge.  Check periodically to make sure that nothing is leaking out of the bottom. Let it cure overnight.

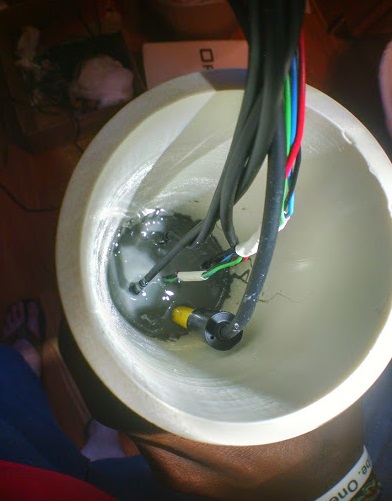
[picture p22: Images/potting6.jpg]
Epoxy potting on the inside of the housing
&nbsp;&nbsp;&nbsp;&nbsp;&nbsp;&nbsp;&nbsp;&nbsp;&nbsp;&nbsp;&nbsp;&nbsp;
 
&nbsp;&nbsp;&nbsp;&nbsp;&nbsp;&nbsp;&nbsp;&nbsp;&nbsp;&nbsp;&nbsp;&nbsp;*Epoxy potting on the inside of the housing.*

### 6.0 Calibration and Data Conversion

Proper calibration of the OpenCTD requires access to already calibrated validation instruments. These can be commercial CTD, handheld systems, or bench-mounted laboratory systems. As the community grows, properly calibrated OpenCTDs can be used to benchmark newly-built instruments. 

#### 6.1 Depth

The pressure sensor outputs absolute pressure, which means that it is self-calibrating. At sea level, pressure should be approximiately 1016 millibars, though local weather and small changes in altitude will affect this baseline. In order to minimize the amount of processing that happens onboard the OpenCTD, pressure is measured in millibars (the default output for the current pressure sensor). To convert pressure to depth use the following equation:

D = (P(depth) - P(surface) * 100) / (g * 1000)

Where D is depth in meters; P(depth) is the pressure (in millibars) at depth); P(surface) is the pressure at the surface in millibars; and g is acceleration due to gravity (9.81 m/s^2).

#### 6.2 Temperature

The Cave Pearl Project has provided an excellent guide to thorough temperature sensor calibration: [DS18B20 Calibration: Finally nailed it!](https://edwardmallon.wordpress.com/2016/03/05/ds18b20-calibration-we-finally-nailed-it/). This process may be overkill for most users, but anyone intending to produce replicatable, peer-review ready results should put in the extra time for a comprehensive calibration. 

Calibrating the temperature sensors requires access to an already calibrated instrument. Allow both the OpenCTD and the validation instrument to equilibrate in water for 15 minutes. Take the average of the three OpenCTD temperature outputs and note the difference between that average and the validation instrument. Repeat for a fluid that is at least 15 degrees hotter or colder than the test fluid. There should be a linear relationship between the OpenCTD temperature sensors and the validation instrument, which will give you a calibration constant. Take the average of the three temperature readings and use the calibration constant to adjust temperature measurements when processing raw data. 

This should remain steady for many casts, but it is always good practice to check you temperature calibration whenever you have access to a validation instrument. We recommend recalibrating temperature at the beginning of each expedition and once a month for prolonged deployments. 

#### 6.3 Conductivity

Calibration of the coductivity meter requires a calibration standard--a bottle of water of precise, known salinity. Calibration is done through software and is explained in detail [here](http://www.atlas-scientific.com/_files/_datasheets/_circuit/EC_EZO_Datasheet.pdf). You can perform either a one or two solution calibration depending on how many standards you have access to. 

To increase the ease of calibration, we [have created a small program for accessing the serial monitor](https://github.com/OceanographyforEveryone/OpenCTD/tree/master/simple_serial_for_EC_calibration). Flash this simple serial program to your Qduino Mini. 

Open the serial monitor through the Arduino IDE. You should see a stream of unprecessed data. 

- Enter **c,0** into the command line and hit enter. This will turn off continuous monitorring.
- Enter **k,?** this will tell you what the K-value of you probe is set to. It should ke set to K=1.0 for most use cases. 
  - To change the K-value, enter **k,x** where **x** is the new K-value of the probe. 
- With the probe dry (be sure there is abosolutely no water on the electrodes) enter **cal,dry**. This will dry calibrate the probe. 
- For 1-point calibration, suspend the probe in calibration solution. Enter **cal,one,y**, where **y** is the known value of the standard. 
- For two point calibration, suspend the probe in the less conductive solution and enter **cal,low,y**, where **y** is the known value of the standard. Then suspend in the more conductive solution and enter **cal,high,z**, where **z** is the known value of the solution. 
- Now enter **c,1** to turn continuous monitorring back on. 

Don't forget to reflash the [OpenCTD software](https://github.com/OceanographyforEveryone/OpenCTD/tree/master/OpenCTD_qDuino) to the Qduino Mini after calibration is done. Conductivity should be recalibrated at least once per year. 

Converting conductivity to PSU is a complex equation that is temperature dependent. This [UNESCO paper](http://unesdoc.unesco.org/images/0005/000598/059832eb.pdf) outlines the basic equations. We are working on an Excel template that will perform those conversions for you. The [OpenCTD_DataConversion_Template](https://github.com/OceanographyforEveryone/OpenCTD/blob/master/Data_Processing/OpenCTD_DataConversion_Template.xlsx) will take raw data from the OpenCTD and make these conversions for you. 

### 7.0 Your first cast. 

This is the fun part. 

For shallow deployments (<100 m), the test cap will keep water out. For deeper deployments (<100 m), pressure compensate the housing with mineral oil or similarly no-conductive fluid. 

**No Mineral Oil:** Ensure that the inside surface of the PVC pipe is clean and free of debris. Hairs can be particularly difficult to see. Seat the test cap onto the housing and tighten the wingnut. Wingnut should be as tigh as possible without tool assistance and the cap should not move or turn. 

**Mineral Oil:** Fill to a few centimeters below the top. There may be some spillover to avoid bubbles in the housing. Turn on the CTD. Gently lower the test cap down and screw it into place. It should be tight enought that it cannot be removed without unscrewing. Your CTD is now sealed and logging. Wipe down any spilled oil. These [microfiber cloths from Amazon](http://amzn.to/2xAVyjg) do a great job of sopping up small amounts of mineral oil. 

Your OpenCTD is now ready to take the plunge! Gently lower into the water and descend no more than 1 meter per second. The slower the better. For the first cast, descend to 5 meters, then recover and check that no leakage has occured. With mineral oil, it will be very clear if the device is leaking. Once it passes the first soak test, you're ready to go forth and collect ocean data. 

Welcome to the Oceanography for Everyone community!

### 8.0 Resources

[Oceanography for Everyone](http://oceanographyforeveryone.com/)

### 9.0 Partners and Projects

If you are building you're own OpenCTD or have recieved one of ours, please add yourself to the following list. 

Partner | Affiliation | Project | Location | Link | Other Contact Info
---|---|---|---|---|---
Ian Black | Oregon State University | CTDizzle |USA | http://blogs.oregonstate.edu/ianblack/ | [@Ian_CTDizzle](https://twitter.com/Ian_CTDizzle)
Jonny Teague | University of Bristol | | England | |[@jonny_teague](https://twitter.com/jonny_teague)  
Steve Haan | | PiCTD | | | [@HaanHouse](https://twitter.com/HaanHouse)

### 10.0 Acknowledgments

This software has been compiled by [Andrew Thaler](https://github.com/SouthernFriedScientist), based on code from Walt Holm, arduino.cc samples, Atlas Scientific, [Vhati](https://github.com/Vhati), and [Russell Neches](https://github.com/orgs/OceanographyforEveryone/people/ryneches). OpenCTD was initially designed by Andrew Thaler, [Kersey Sturdivant](https://github.com/goldsphininx), and Russell Neches. 

### 11.0 Code of Conduct

Please review our [Contributor Code of Conduct](https://github.com/OceanographyforEveryone/OpenCTD/blob/master/CODE_OF_CONDUCT.md) prior to your first contribution.

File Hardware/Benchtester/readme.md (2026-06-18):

## OpenCTD Benchtest Board

Congratulations! If you've landed here, you've recieved one of the OpenCTD benchtest boards/calling cards. This card allows you to build a working OpenCTD based on the [Rev7](https://github.com/OceanographyforEveryone/OpenCTD/tree/main/Retired/OpenCTD_Rev7) that you can use to practice your soldering skills, test OpenCTD components before permanently sealing them into epoxy, or build a benchtop instrument for measuring  salinity, temperature, and air pressure. This board works with the components listed in the OpenCTD Rev7 manual [Construction and Operation of the OpenCTD](https://github.com/OceanographyforEveryone/OpenCTD/blob/main/Retired/OpenCTD_Rev7/Documentation/OpenCTD_ConstructionOperation.pdf). 

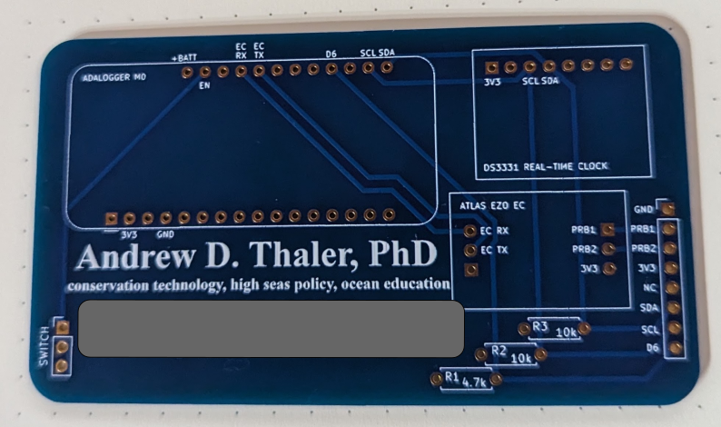
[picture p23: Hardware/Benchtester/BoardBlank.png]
Bare OpenCTD Benchtest Board


To build your benchtester, you will need:
1. [Standard female headers](https://amzn.to/3J5v8dg) (2 8-pin headers, 2 3-pin headers, 1 16-pin header, and 1 12-pin header, but you can order long strips of headers and cut them down with a flush cutter)
2. [10 kOhm resistors](https://amzn.to/4cN27Rc) (2)
3. [4.7 kOhm resistor](https://amzn.to/4aIREVb) (1)
4. [2-position board mounted switch](https://www.adafruit.com/product/805) (1)

The only tools and consumables you need are a [soldering iron](https://amzn.to/4aios7I), [solder](https://amzn.to/4cMaoVF), and [flush cutters](https://amzn.to/4cDmFf0). I love the Pinecil as a simple starter soldering iron. You will need to get a [power supply](https://amzn.to/3J8Vewa) for the Pinecil. 

This board is designed to work with the [Adafruit Adalogger M0 Feather](https://www.adafruit.com/product/2796), the [Atlas EZO EC conductivity circuit](https://amzn.to/49nwWcp), and the [DS3231 Real-Time Clock](https://www.adafruit.com/product/5188). If you have an OpenCTD kit, all three components are already included. 

Once assembled, this board will read data from the [Sparkfun 14-Bar Pressure Sensor Breakout Board](https://www.sparkfun.com/products/12909) (or any other system using a MS5803-14BA pressure chip), any [DS18B20 temperature sensor](https://amzn.to/49sBpL5), and any [two-electrode conductivity probe](https://amzn.to/3xrnmrT).

### Assembling the Benchtest Board

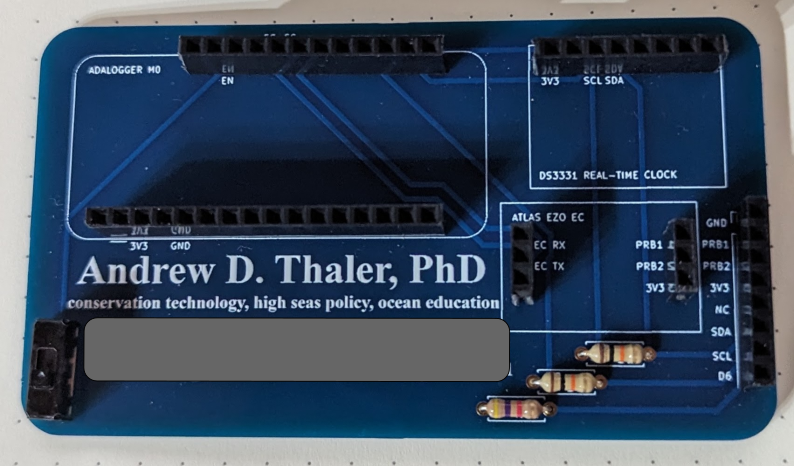
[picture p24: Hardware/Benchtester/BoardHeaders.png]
OpenCTD Benchtest Board with headers, switch, and resistors


Note: All components will be soldered onto on the front (the side with Andrew's contact information) of the card. If you've never soldered before, I recomend reading through Mitch Altman's [Soldering Is Easy](https://mightyohm.com/files/soldercomic/FullSolderComic_EN.pdf) guide. 

1. Trim your strips of female headers to the correct length for each set of through holes. I reccommend cutting through the center of the next pin in the line in order to ensure that you do not accidentally cut it too short. You will have 1 16-pin-long strip, 1 12-pin-long strip, 2 8-pin long strips, and 2 3-pin-long strips.

2. Solder each strip of pins into the corresponding row that they fit in. The 16- and 12-pin strips will go in the rows for the Adalogger M0. The 3-pin strips will go in teh rows for the Atlas EZO EC. One 8-pin strip will go in the row for the DS3231 Real-Time Clock (on some boards it may be mislabelled DS 3331). The final 8-pin strip will go on the row of 8 labeled holes on the lower right edge of the card.

3. Insert the 4.7 kOhm resistor through the holes labeled R1. It does not matter which leg of the resistor goes through which hole. Solder in place. 

4. Insert the two 10 kOhm resistors through the holes labeled R2 and R3. It does not matter which leg of the resistor goes through which hole. Solder in place.

5. Insert the switch into the holes labeled switch and solder into place.

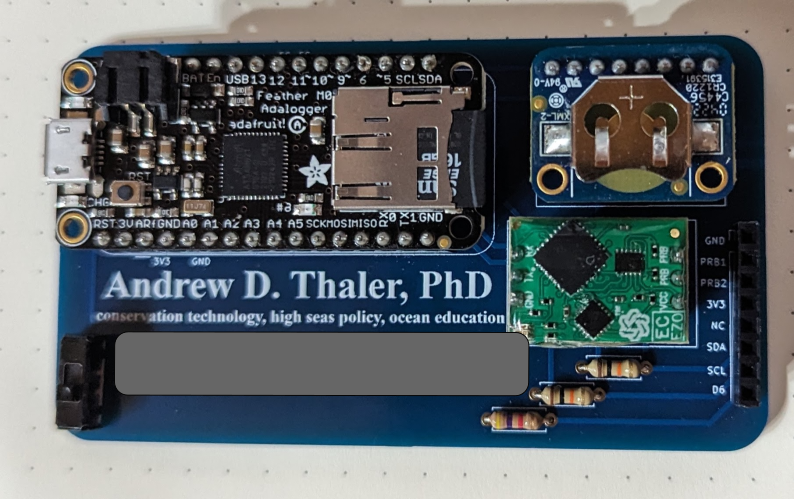
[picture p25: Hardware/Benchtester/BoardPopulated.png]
OpenCTD Benchtest Board populated with components


That's it! Your board is now ready to be populated with OpenCTD components. For instuctions on how to assemble the Adalogger, Real-time Clock, and EZO EC circuit, as well as the sensors, please refer to Chapter 6 and Chapter 7 of [Construction and Operation of the OpenCTD](https://github.com/OceanographyforEveryone/OpenCTD/blob/main/Retired/OpenCTD_Rev7/Documentation/OpenCTD_ConstructionOperation.pdf). To learn how to calibrate these sensor, you can reference the build guide or the [Calibration and Data Management](https://github.com/OceanographyforEveryone/OpenCTD/blob/main/Retired/OpenCTD_Rev7/Documentation/OpenCTD_CalibrationDataManagement.pdf) guide.

Firmware for the retired OpenCTD Rev7 can be found in the [archived directory](https://github.com/OceanographyforEveryone/OpenCTD/tree/main/Retired/OpenCTD_Rev7/Firmware)

OpenCTD Benchtest Board with sensors attached

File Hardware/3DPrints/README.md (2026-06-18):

# OpenCTD Shapefiles
This directory contains all the 3D printer shapefiles needed to assemble an OpenCTD Rev8.

## Baseplates (print with 100% infill to avoid voids where water may enter)
- [OpenCTD_Rev8_Baseplate_CPS](https://github.com/OceanographyforEveryone/OpenCTD/blob/main/Hardware/3DPrints/OpenCTD_Rev8_Baseplate_CPS.3mf): Baseplate for the Rev8 OpenCTD using an Oceanography for Everyone Custom Pressure Sensor Breakout Board.
- [OpenCTD_Rev8_Baseplate_SF](https://github.com/OceanographyforEveryone/OpenCTD/blob/main/Hardware/3DPrints/OpenCTD_Rev8_Baseplate_SF.3mf): Baseplate for the Rev8 OpenCTD using a Spark Fun Pressure Sensor Breakout Board.
- [OpenCTD_Rev8_Baseplate_IMU](https://github.com/OceanographyforEveryone/OpenCTD/blob/main/Hardware/3DPrints/OpenCTD_Rev8_Baseplate_IMU.3mf): Baseplate for the Rev8 OpenCTD using an OpenROV IMU.

## PowerSquid Chassis (print with 50% infill to maximize strength and print speed)
- [OpenCTD_Rev8_Chassis_Top](https://github.com/OceanographyforEveryone/OpenCTD/blob/main/Hardware/3DPrints/OpenCTD_Rev8_Chassis_Top.3mf): The top section of the PowerSquid electronics chassis.
- [OpenCTD_Rev8_Chassis_Bottom](https://github.com/OceanographyforEveryone/OpenCTD/blob/main/Hardware/3DPrints/OpenCTD_Rev8_Chassis_Bottom.3mf): The bottom section of the PowerSquid electronics chassis.
- [OpenCTD_Rev8_Chassis_Cap](https://github.com/OceanographyforEveryone/OpenCTD/blob/main/Hardware/3DPrints/OpenCTD_Rev8_Chassis_Cap.3mf): The end cap for the PowerSquid electronics chassis. 

## Router Jigs (print with 100% infill for maximum durability)
- [Router_Jig_for_Housing_1](https://github.com/OceanographyforEveryone/OpenCTD/blob/main/Hardware/3DPrints/Router_Jig_for_Housing_1.3mf): Router jig to cut the initial notch in the PVC housing.
- [Router_Jig_for_Housing_2](https://github.com/OceanographyforEveryone/OpenCTD/blob/main/Hardware/3DPrints/Router_Jig_for_Housing_2.3mf): Router jig to cut the second and third notch in the PVC housing.

## Accessories (print with 50% infill to maximize strength and print speed)
- [Cap_Wrench](https://github.com/OceanographyforEveryone/OpenCTD/blob/main/Hardware/3DPrints/Cap_Wrench.3mf): Wrench for tightening and loosening the plumbers test cap on the OpenCTD.

*3D printer shapefiles updated 6/17/2026 for compatibility with the Rev8 control board.*

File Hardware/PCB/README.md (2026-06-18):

# OpenCTD PCB

The OpenCTD main board is designed using [KiCad](https://www.kicad.org/).

The current [OpenCTD]() uses the [OpenCTD Rev8 control board](). Previous generation control boards are archived in [Retired](https://github.com/OceanographyforEveryone/OpenCTD/tree/main/Retired). 

The Oceanography for Everyone Custom Pressure Sensor breakout board ([Ofe_CPS](https://github.com/OceanographyforEveryone/OpenCTD/blob/main/Hardware/PCB/OfE_CPS.zip)) allows you to build an inexpensive version of the Sparkfun Breakout Board, but requires advanced soldering techniques.

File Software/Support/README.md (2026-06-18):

This folder contains support code for the OpenCTD. 

In [Arduino Libraries](https://github.com/OceanographyforEveryone/OpenCTD/tree/main/Software/Support/Arduino%20Libraries), you will find compressed .zip files for all of the libraries required to run the OpenCTD software that do not come bundled with Arduino. These include:

- [Adafruit_MAX31865.zip](https://github.com/OceanographyforEveryone/OpenCTD/blob/main/Software/Support/Arduino%20Libraries/Adafruit_MAX31865.zip) which allows you to communicate with the temperature sensor array.
- [MS5803_14.zip](https://github.com/OceanographyforEveryone/OpenCTD/blob/main/Software/Support/Arduino%20Libraries/MS5803_14.zip) which supports the 14-bar pressure sensors.
- [RTClib.zip](https://github.com/OceanographyforEveryone/OpenCTD/blob/main/Software/Support/Arduino%20Libraries/RTClib.zip) which drives the real-time clock.
- [SoftwareSerial.zip](https://github.com/OceanographyforEveryone/OpenCTD/blob/main/Software/Support/Arduino%20Libraries/SoftwareSerial.zip) which enables the serial monitor on the Adafruit Adalogger.

In addition, you will find [Serial_for_EC_Calibration_m0](https://github.com/OceanographyforEveryone/OpenCTD/tree/main/Software/Support/Serial_for_EC_Calibration_m0) which allows you to calibrate the OpenCTD's conductivity circuit through the Arduino IDE terminal and [RTC_Reset](https://github.com/OceanographyforEveryone/OpenCTD/tree/main/Software/Support/RTC_Reset) which resets the real-time clock to the last system time when the software was compiled. 

Please reference the [OpenCTD Construction and Operation Manual](https://github.com/OceanographyforEveryone/OpenCTD/blob/main/Documentation) for a full description of how to import and use this software.

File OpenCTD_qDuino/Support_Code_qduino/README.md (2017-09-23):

Support Code
============

Here you will find supplemental software to simplify building and testing the OpenCTD. 

[**MS5803_14_test**](https://github.com/OceanographyforEveryone/OpenCTD/tree/master/Support_Code/MS5803_14_test) reads just the pressure sensor in standard configuration so that your can confirm its functionality.

[**TempProbeTester**](https://github.com/OceanographyforEveryone/OpenCTD/tree/master/Support_Code/TempProbeTester) allows users to batch test up to 24 temperature probes to check quality and accuracy before installation. 

[**simple_serial_for_EC_calibration**](https://github.com/OceanographyforEveryone/OpenCTD/tree/master/Support_Code/simple_serial_for_EC_calibration) allows users to calibrate the Altas EZO conductivity circuit.

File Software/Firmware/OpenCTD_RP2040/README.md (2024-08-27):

We are in the process of updating the OpenCTD firmware to run on CircuitPython on the new RP 2040 Adalogger. 

Download a working library for the [MS5803-14Ba pressure sensor](https://github.com/OceanographyforEveryone/OpenCTD/tree/main/Software/Firmware/OpenCTD_RP2040/MS5803-14BA) based on code adapted from [Sparkfun](https://github.com/sparkfun/MS5803-14BA_Breakout) and [Minyiky](https://github.com/minyiky/ms5803-micropython).

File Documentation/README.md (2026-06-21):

## OpenCTD Primary Documentation

The Sixth Edition of the OpenCTD Construction and Operation Manual is live as of June 20, 2026!  

- [Construction and Operation of the OpenCTD Rev8](https://github.com/OceanographyforEveryone/OpenCTD/blob/main/Documentation/OpenCTD_ConstructionOperation_REV8.pdf). The ultimate guide for building, calibrating, testing, and deploying your own OpenCTD. To download .pdfs from GitHub, click on the link and then click "download raw file" in the upper right corner below the "history" icon. 
- [Construction and Operation of the OpenCTD Rev8](https://oceanographyforeveryone.com/wp-content/uploads/2026/06/OpenCTD_ConstructionOperation_REV8.pdf), mirrored on the [Oceanography for Everyone](http://oceanographyforeveryone.com/) homepage.

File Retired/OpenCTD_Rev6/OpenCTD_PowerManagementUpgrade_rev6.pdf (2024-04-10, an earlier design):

# OpenCTD Power Management Upgrade

One of the more frustrating problems with the current OpenCTD is that in order to charge, the device must be turned on. This is due to the use of an electromechanical switch that breaks contact with the battery to power down the device. The design results in users failing to charge their device if they forget to turn it on or producing massive, empty data files if their OpenCTD is left on and charging for long period of time. This is bad design. We can fix it.
Fortunately, we have developed a solution that has be implemented in the next revision of the OpenCTD carrier board. Unfortunately, almost all of the carrier boards currently in circulation are the OpenCTD rev 6 carrier boards with the annoying charging protocol. The good news is that we have a workaround.
If you have an OpenCTD custom carrier board labeled OpenCTD 7c, congratulations, you have the new and improved board. There are a few changes to the current build guide (Construction and Operation of the OpenCTD, Fourth Edition) that will make the build a tiny bit simpler. In Chapter 8
- Power the CTD, you can ignore steps 2 and 3, the two pins labeled J1 no longer exist and the power is routed through board to the EN pin on the Adalogger M0, the switch is also in a slightly different location.


Figure 1. OpenCTD 7c carrier board (board color can vary).
If you have an OpenCTD custom carrier board labeled OpenCTD rev 6, then you have the older power management solution that only charges the battery when the entire device is turned on. There are a few steps involved in re-routing the power management to make the board charge while the batteries are off. You will have to solder jumper wires between a few pins and break the trace which connects the Atlas EZO EC chip to the battery. To do this, you will need a knife, a soldering iron, wire cutters, and some short solid core or stranded wire to jump the pins.


Figure 2. OpenCTD rev 6 carrier board (board color can vary).
It is easiest to do this after you’ve populated the custom carrier board with header in Chapter 6.2 Prepare the Carrier Board.
Rerouting power to the Atlas EZO EC Chip.

The first step is to break the connection between the Atlas EZO EC chip and the battery so that you can connect it directly to the 3V3 output on the Adalogger M0.
1. Expose the +BATT trace under the Atlas EZO EC chip. Using a knife scrape away the coating over the large trace that runs from the pin labeled +BATT on space the Atlas EZO EC chip. This trace is the only trace on the topside of the board between the two 3-pin headers for the EZO EC chip. You will know that you have scraped down far enough when you reveal the bare copper underneath.

### 2. Break the +BATT trace under the Atlas EZO EC chip. Using the same knife, scrape away

the copper trace, as shown in figure 3, to break the connection between the EZO EC chip and the battery.


Figure 3. OpenCTD rev 6 board populated with headers, resistors, and the 3-pin switch, with the trace connecting the Atlas EZO EC chip to the battery pin broken.

3. Jump the +BATT pin to the 3V3 pin for the Adalogger M0. On the reverse side of the board, solder a lead wire to the +BATT pin for the Atlas EZO EC chip and the pin labeled 3V3 on the headers for the Adalogger M0. Refer to figure 4 below.

## Redirecting the 3-pin toggle switch to GND and EN

Neither GND nor EN are labeled on the Rev 6 custom carrier board, but both are labeled on their corresponding pins on the Adalogger M0, which can be used for reference.
GND is the fourth pin from the left on the longer of the two pin rows for the Adalogger M0. If you flip the board over, you will see that the traces for the GND pin form an X, connecting the pin to the universal ground for the board.
EN is the second pin from the left on the shorter of the two pin rows for the Adalogger M0. It is next to the pin labeled +BATT. EN is short for “engage” and it is a signal pin which tells the board to turn on when the pin is connected to GND.
1. Connect one of the pins labeled J1 to GND. It does not matter which of the J1 pins you route to the pin labeled GND on the headers to the Adalogger M0. Refer to figure 4 below.
2. Connect one of the pins labeled J1 to EN. Route the unused J1 pin to the header pin for EN, which is to the right of the pin labeled +BATT. This pin is unlabeled on the carrier board but its corresponding pin on the Adalogger M0 is labeled. Refer to figure 4 below.


Figure 4. Reverse side of OpenCTD rev 6 carrier board with the necessary jumper cables to enable power of charging.
Your board is now ready to charge, even when powered down. Populate the board with components according to the manual and plug the battery directly into the JST connector. You no longer need to cut the battery wire.
Congratulations, you’ve just hacked your OpenCTD for improved functionality!
A new 3D printable chassis will shortly be available on the OpenCTD GitHub Repository. It replaces the existing chassis and work with either board.

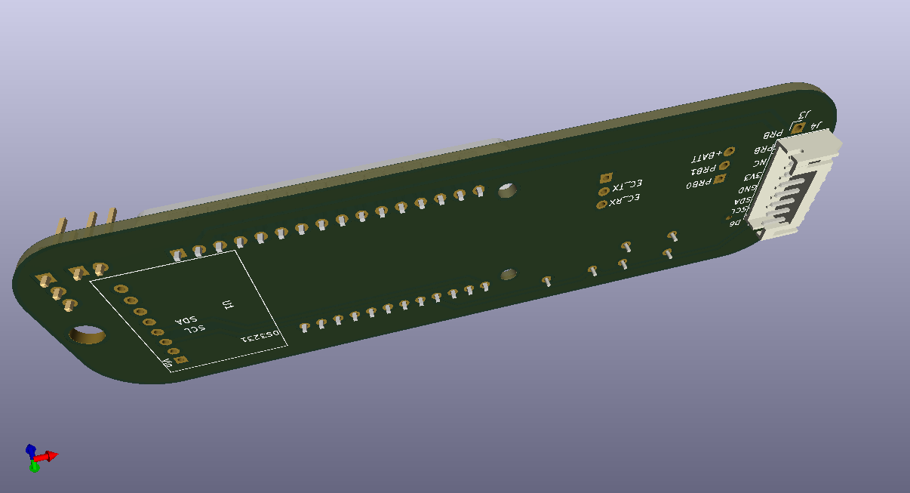
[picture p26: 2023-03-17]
Hardware/PCB/rev6/kicad-openctd-rev6/fab/kicad-openctd-3d-3.png

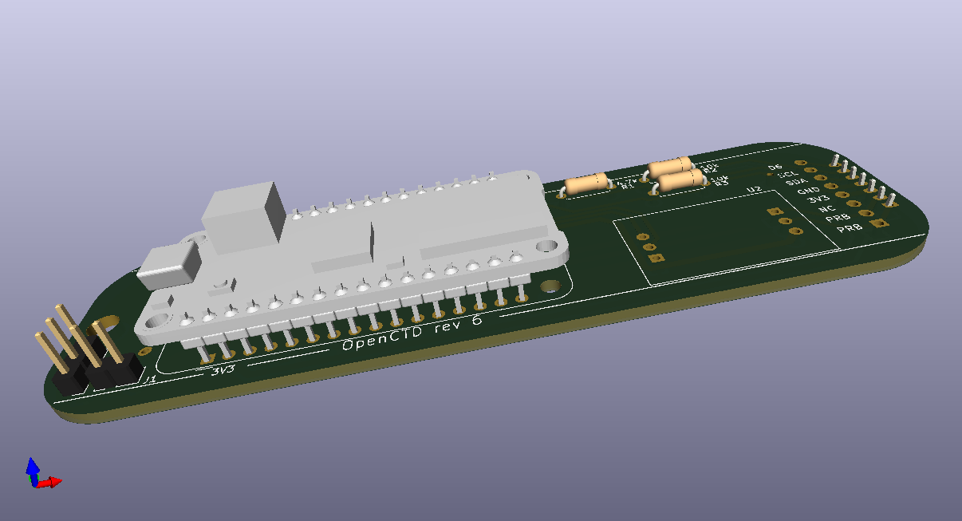
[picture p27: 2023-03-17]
Hardware/PCB/rev6/kicad-openctd-rev6/fab/kicad-openctd-3d-1.png

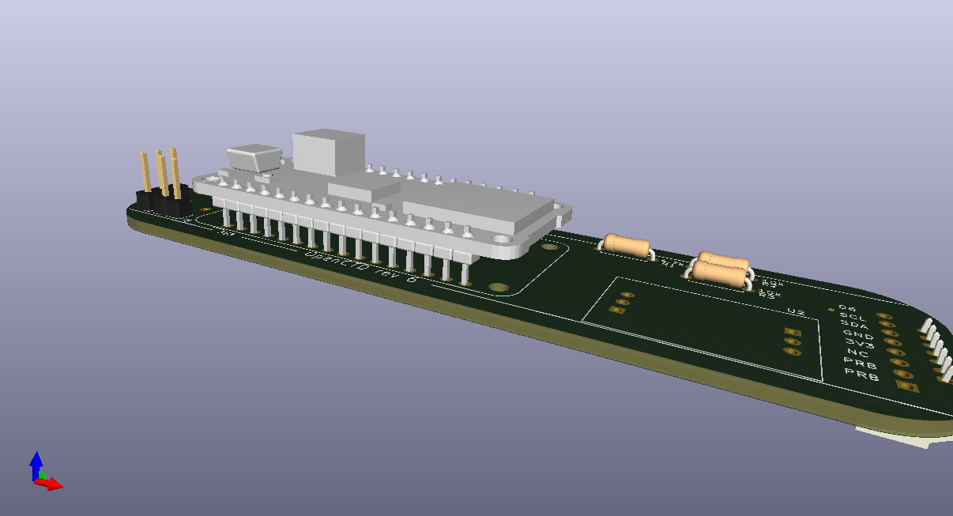
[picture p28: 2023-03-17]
Hardware/PCB/rev6/kicad-openctd-rev6/fab/kicad-openctd-3d-2.png

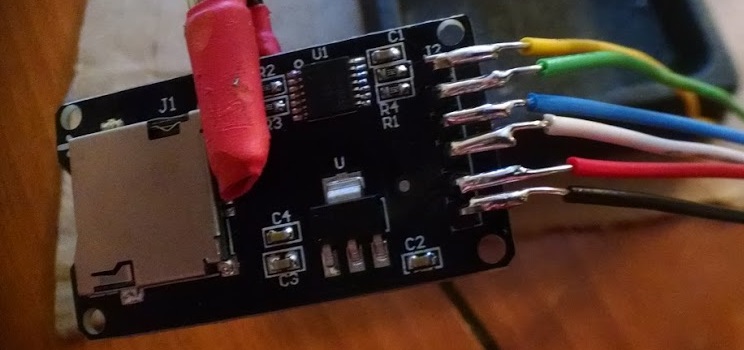
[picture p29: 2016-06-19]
Documentation/Images/SD2.jpg

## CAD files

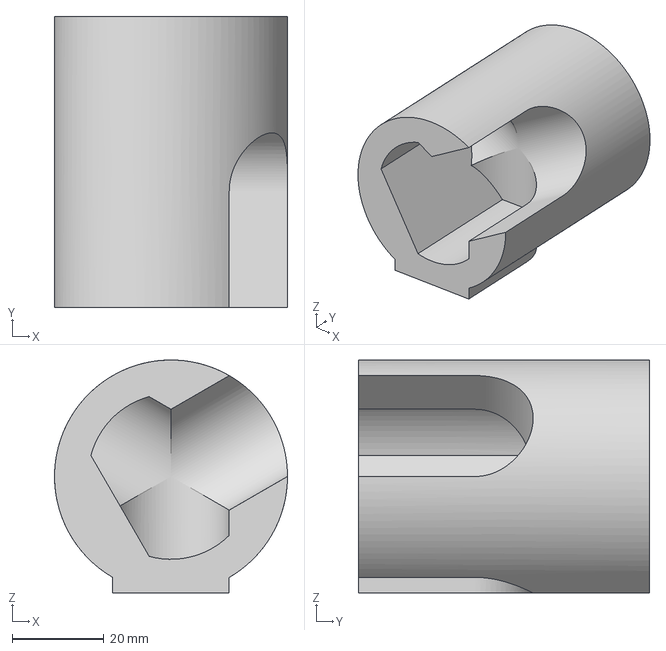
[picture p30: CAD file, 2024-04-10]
Hardware/3DPrints/Models/Accessories/RouterJigForHousing2.3mf
50.8 x 63.5 x 50.8 mm

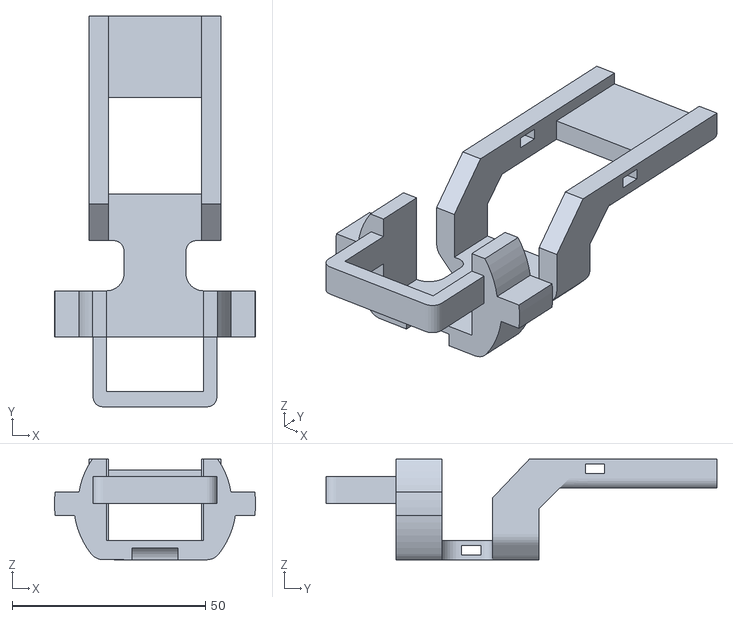
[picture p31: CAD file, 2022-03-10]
Hardware/3DPrints/Models/Alternatives/OpenCTD_ElectronicsChassis_M0_Reinforced_Switch.stl
52.0 x 101.0 x 26.0

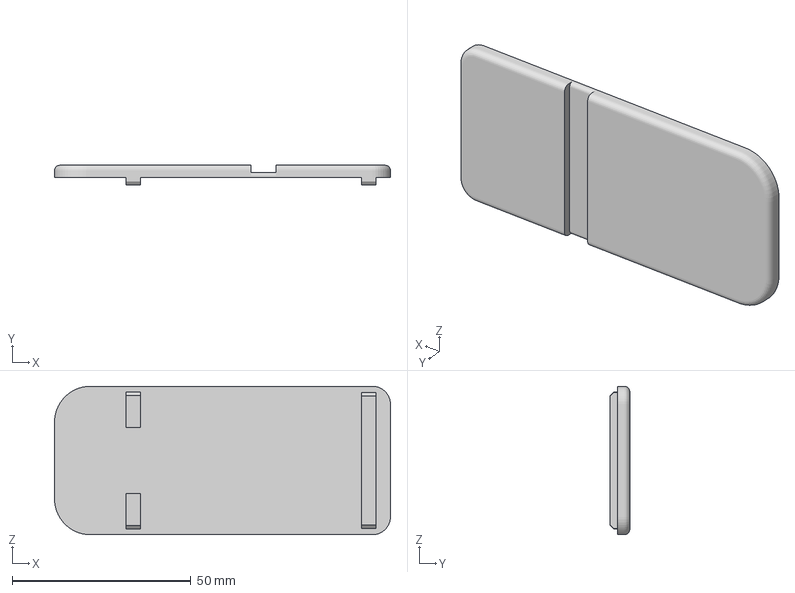
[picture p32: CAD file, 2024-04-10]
Hardware/3DPrints/Models/OpenCTD_ElectronicsChassis_Bottom.3mf
94.0 x 5.50 x 41.5 mm

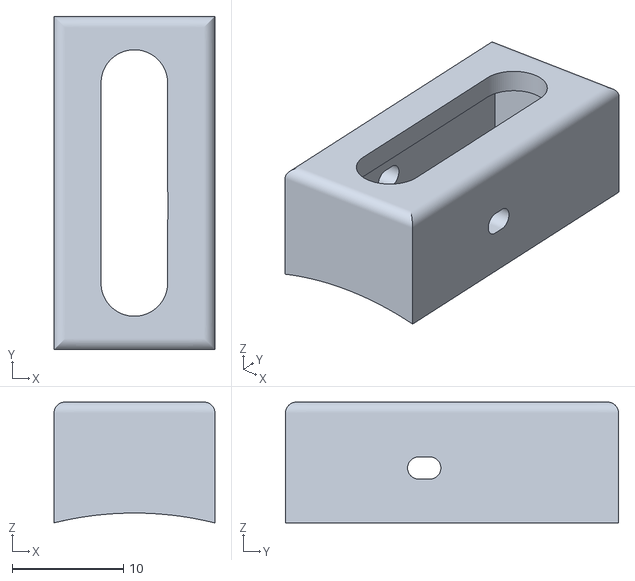
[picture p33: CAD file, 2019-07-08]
Hardware/3DPrints/Models/Optional Magnetic Switch/OpenCTD_MagneticSwitch_External_M0.stl
14.5 x 30.0 x 10.9

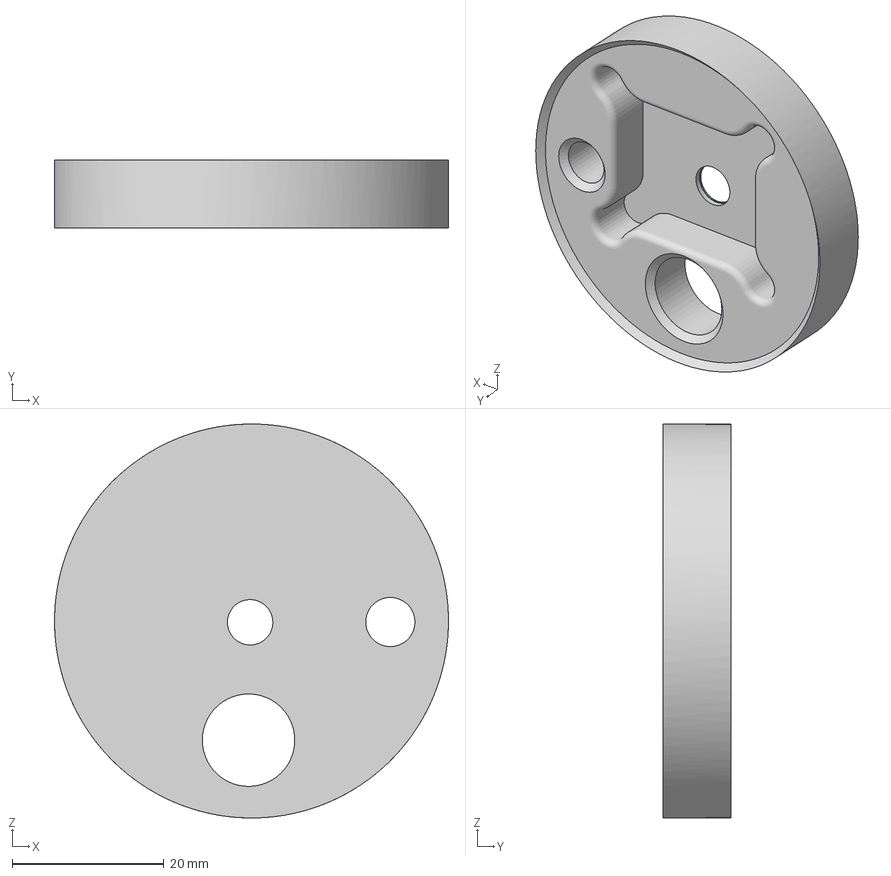
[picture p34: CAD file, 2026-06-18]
Hardware/3DPrints/OpenCTD_Rev8_Baseplate_SF.3mf
52.0 x 9.00 x 52.0 mm

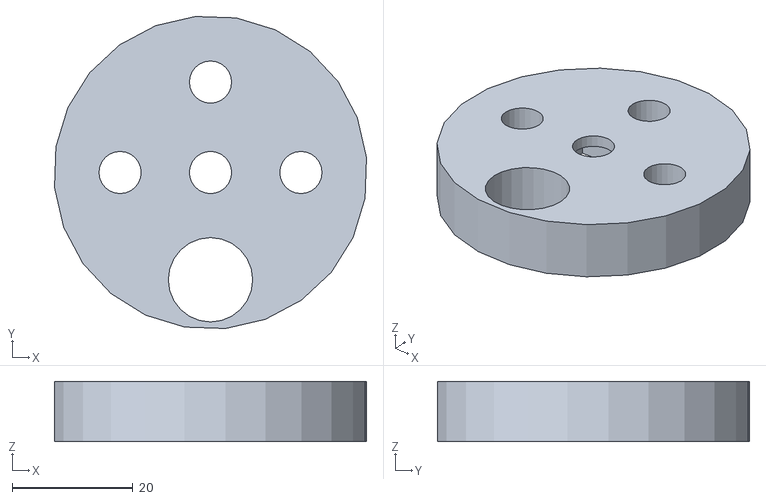
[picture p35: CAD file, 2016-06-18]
OpenCTD_qDuino/3D_Printer_Files_qduino/OpenCTD_2in.stl
51.8 x 51.8 x 10.0

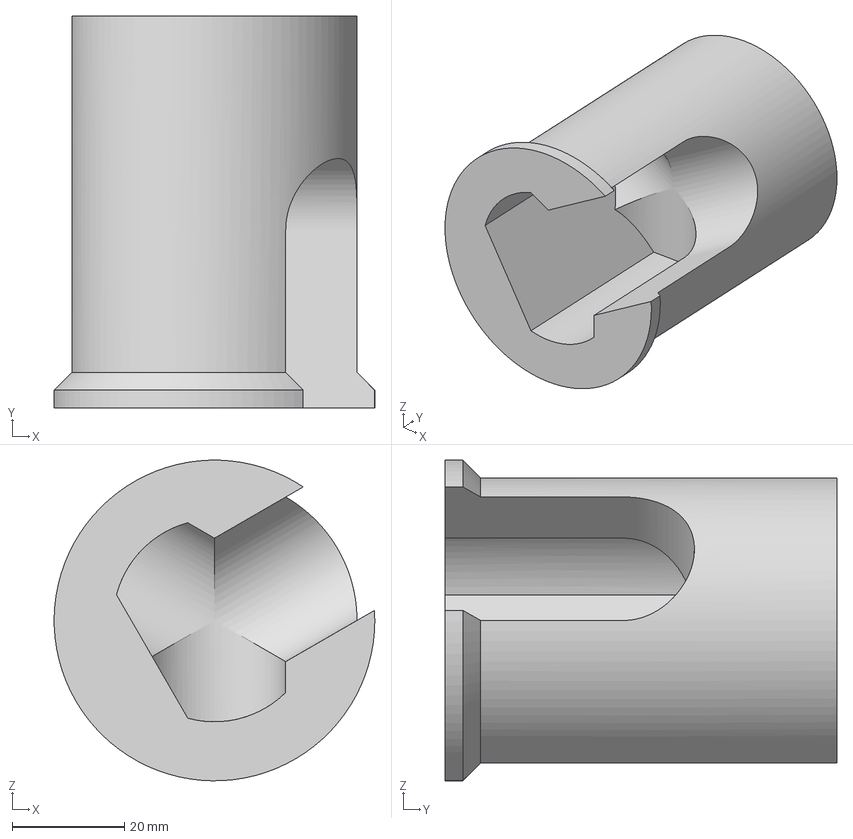
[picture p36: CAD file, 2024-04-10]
Hardware/3DPrints/Models/Accessories/RouterJigForHousing1.3mf
57.1 x 69.8 x 57.1 mm

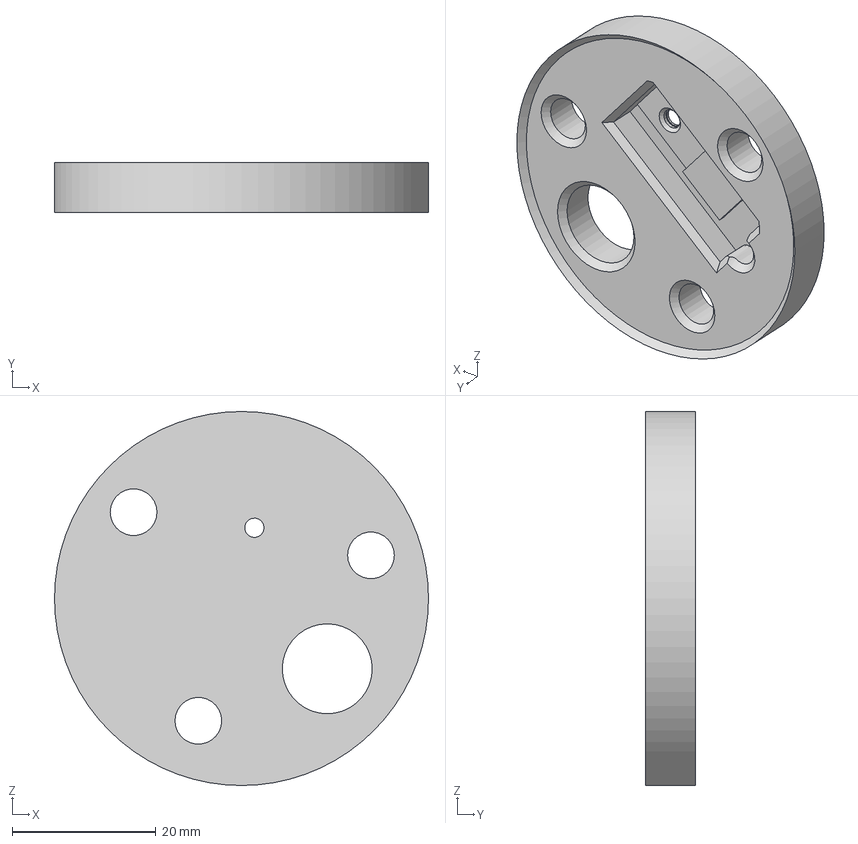
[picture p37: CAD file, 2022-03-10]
Hardware/3DPrints/Models/Alternatives/OpenCTD_M0_Baseplate_OpenROV_IMU.3mf
52.0 x 7.00 x 52.0 mm

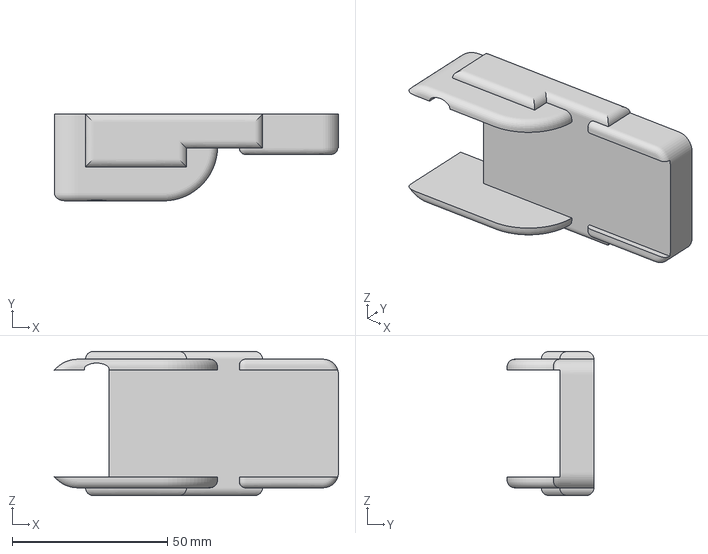
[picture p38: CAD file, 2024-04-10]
Hardware/3DPrints/Models/OpenCTD_ElectronicsChassis_Top.3mf
91.6 x 28.0 x 46.5 mm

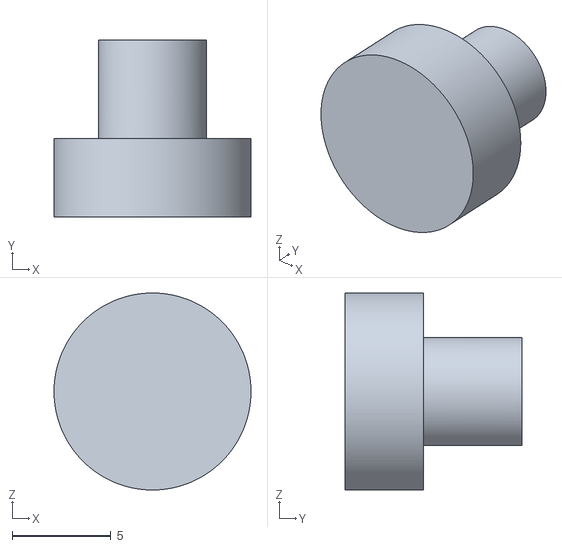
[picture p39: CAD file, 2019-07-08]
Hardware/3DPrints/Models/Optional Magnetic Switch/OpenCTD_MagneticSwitch_Pin_M0.stl
10.0 x 9.00 x 10.0

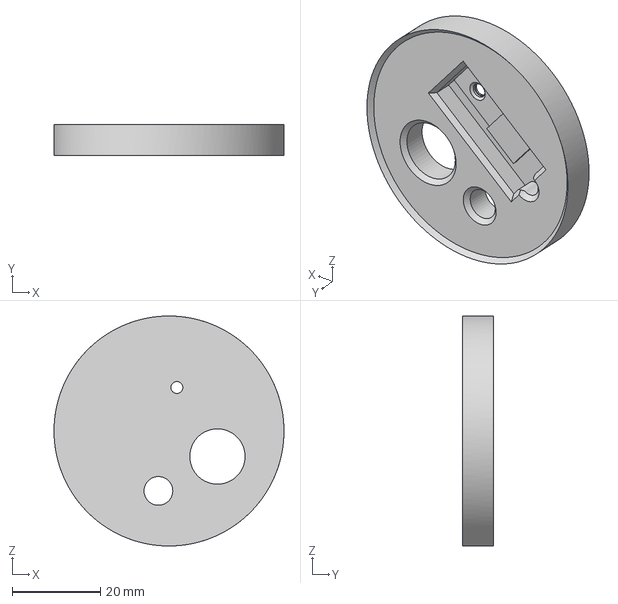
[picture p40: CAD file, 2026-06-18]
Hardware/3DPrints/OpenCTD_Rev8_Baseplate_IMU.3mf
52.0 x 7.00 x 52.0 mm

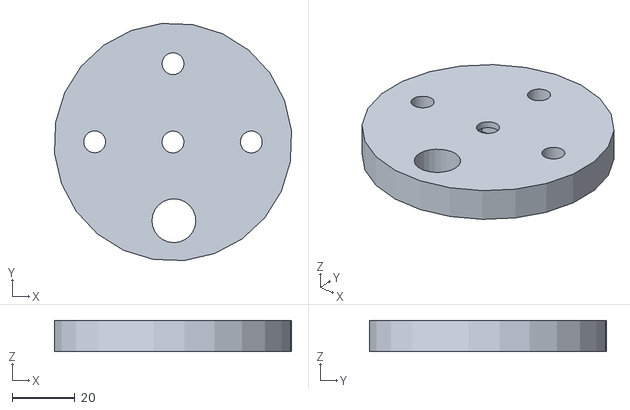
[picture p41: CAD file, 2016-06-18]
OpenCTD_qDuino/3D_Printer_Files_qduino/OpenCTDv4.stl
75.6 x 75.6 x 10.0

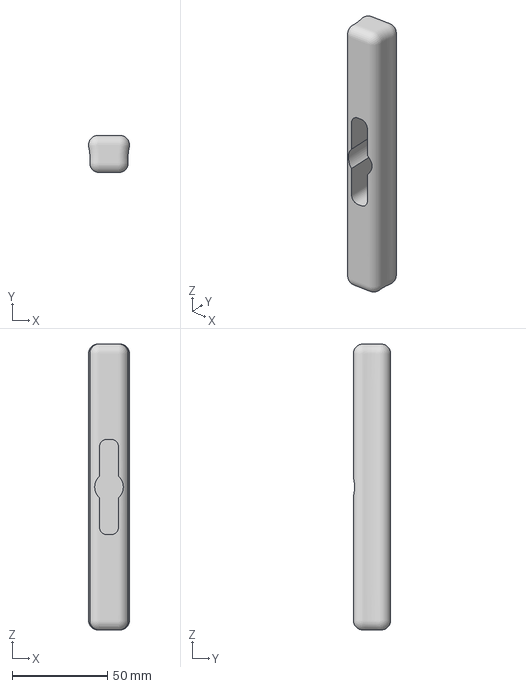
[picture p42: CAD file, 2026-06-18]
Hardware/3DPrints/Cap_Wrench.3mf
21.5 x 19.5 x 150.0 mm

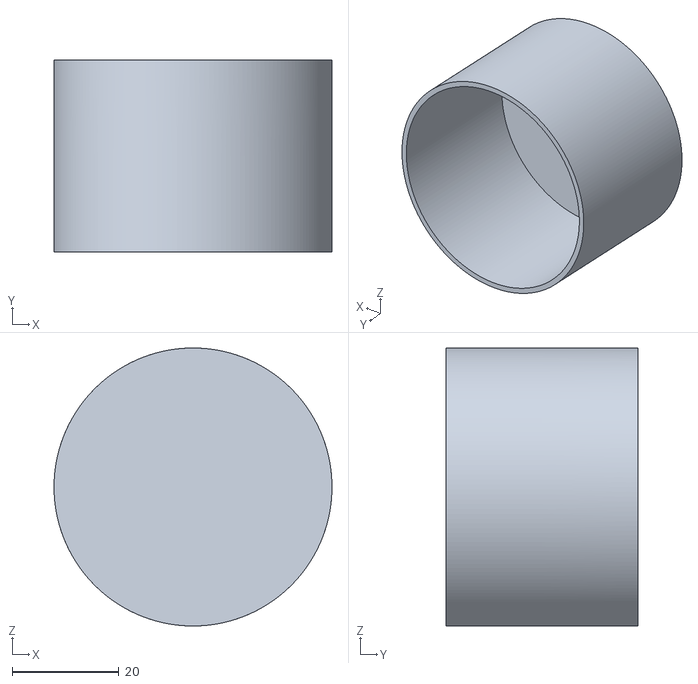
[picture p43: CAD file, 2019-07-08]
Hardware/3DPrints/Models/Accessories/2-inch_PVC_PaintCap_Bottom.stl
52.0 x 36.0 x 52.0

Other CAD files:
Hardware/3DPrints/Models/Alternatives/OpenCTD_Connector_M0.stl
Hardware/3DPrints/Models/Optional Magnetic Switch/OpenCTD_MagneticSwitch_Internal_M0.stl
Hardware/3DPrints/Models/Accessories/2-inch_PVC_PaintCap_Top.stl
Hardware/3DPrints/OpenCTD_Rev8_Baseplate_CPS.3mf
Hardware/3DPrints/OpenCTD_Rev8_Chassis_Bottom.3mf
Hardware/3DPrints/OpenCTD_Rev8_Chassis_Cap.3mf
Hardware/3DPrints/OpenCTD_Rev8_Chassis_Top.3mf
Hardware/3DPrints/Router_Jig_for_Housing_1.3mf
Hardware/3DPrints/Router_Jig_for_Housing_2.3mf
OpenCTD_qDuino/3D_Printer_Files_qduino/OpenCTD_2in.skp
OpenCTD_qDuino/3D_Printer_Files_qduino/OpenCTDv4.skp
Retired/OpenCTD_Rev5/3D_Printer_Files_qduino/OpenCTD_2in.skp
Retired/OpenCTD_Rev5/3D_Printer_Files_qduino/OpenCTDv4.skp
Retired/OpenCTD_Rev7/3DPrints/Models/Accessories/2-inch_PVC_PaintCap_Top.stl
Retired/OpenCTD_Rev7/3DPrints/Models/Alternatives/OpenCTD_Connector_M0.stl
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

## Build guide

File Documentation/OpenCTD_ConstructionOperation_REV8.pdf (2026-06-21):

# Construction and Operation of the

# OpenCTD

## (Rev8)

OpenCTD: Construction and Operation - 2 oceanographyforeveryone.com

Construction and Operation of the OpenCTD

Andrew Thaler, with contributions from Russell Neches, S. Kersey Sturdivant, Jeff Branson, Andrea Schmuttermair, Brian Marx, and Allie Wilkinson.

Sixth Edition: June 2026.

Cover Art by Andrew Thaler.

Photographs by Andrew Thaler and Allie Wilkinson unless otherwise noted.

Funding to produce this document was provided by a grant from the Open Science Hardware Foundation and support from a Patreon crowdfunding campaign.

This work is licensed under a Creative Commons Attribution-NonCommercial 4.0 International License. (https://creativecommons.org/licenses/by-nc/4.0/)

## Contents

Introduction | 5
Building Skills | 7
Project Status and Compatibility | 8
Acknowledgements | 8
Materials, Tools, and Consumables | 10
OpenCTD Rev8 Parts Checklist | 11
Prepare the Adalogger M0 | 11
Tools and Consumables | 13
Andrew’s Toolkit | 13
Safety | 16
What tools will I encounter? | 16
What chemicals will I encounter? | 17
General Safety | 17
Lithium Polymer Batteries | 17
Electronics | 18
Adalogger M0 Software and Libraries | 18
Required Arduino Libraries | 19
Flash the OpenCTD software to the Adalogger | 20
Prepare the Adalogger M0 | 20
Prepare the Carrier Board | 22
Prepare the Real-Time Clock | 24
Prepare the MAX31865 PT1000 Temperature Amplifier | 25
Assemble the Control Unit | 27
Powering the OpenCTD | 28
Prepare the PT1000 Temperature Probe | 29
Prepare the Sparkfun Pressure Sensor | 30
Prepare the Atlas Conductivity Probe | 30
Test All Components | 32
Housing | 34
3D-printing | 34
Assemble the PowerSquid | 35

Cutting the PVC Housing | 37
Using the router jig | 37
If you don’t have a router table | 41
Building the Sensor Package | 43
Pot the Pressure Sensor | 43
Pot the OpenCTD | 44
Calibration and Data Management | 46
Pressure (Depth) | 46
Temperature | 47
Conductivity (Salinity) | 48
Data Management | 54
Final Preparation and First Deployment | 55
Casting Loop | 55
Weighted Casting Line | 56
Internal Ballast | 57
External Ballast | 58
The First Deployment | 58
Stewardship | 60
Works Cited | 61
Resources and Datasheets | 62
Bill of Materials | 63
Appendix A. Alternate Pressure Sensor | 70
Components for Board Mounted Pressure Sensor | 70
DIY Pressure Sensor | 71

## Introduction

The ocean belongs to everyone. The tools to study the ocean should be accessible to anyone with the curiosity and motivation to pursue that inquiry.

There is something radical about making and using your own scientific instruments. The structure of scientific inquiry has coalesced around a model that is both expensive and exclusive. This centralizes knowledge production within a circle of individuals, organizations, and institutions that rarely reflect the breadth of identities, experiences, and ways of knowing of those most directly connected to the places being explored.

By building your own instruments to study and understand the natural world, by taking ownership over the tools of scientific inquiry, you contribute to expanding this circle of knowledge production. A scientist who can make their own instruments is not beholden to the cycles of funding and access that pervade formal inquiry. A researcher who can repair their own equipment is not dependent on the ever-changing winds of academic sentiment to decide what is and is not worthy of study. A community leader who has the tools to generate their own data does not have to wait for institutions to prioritize an emerging crisis before taking action.

You don’t need to ask for permission to understand your world.

Nowhere is this inequality of access more pronounced than in the ocean sciences, where all but a few entities have the capital to mount major oceanographic research campaigns. Even localized coastal research can be stymied by the need for vessels, equipment, and instruments, access to which is often controlled by research institutions. As the need to understand the dramatic changes happening both at the surface and beneath the waves accelerates, barriers that preclude the participation of ocean stakeholders further erodes our potential to understand, anticipate, and adapt to those changes.

The ocean is not uniform, it its filled with swirling eddies, temperature boundaries, layers of high and low salinity, changing densities, and other physical characteristics invisible to surface observers (Sverdrup et al., 1942). By measuring salinity, temperature, and depth, knowledge seekers can unlock ocean patterns hidden beneath the sea's surface. To reveal these patterns, oceanographers use a CTD—an instrument that measures conductivity (used to calculate salinity), temperature, and absolute pressure (used to determine water depth; Thomson and Emery, 2014).

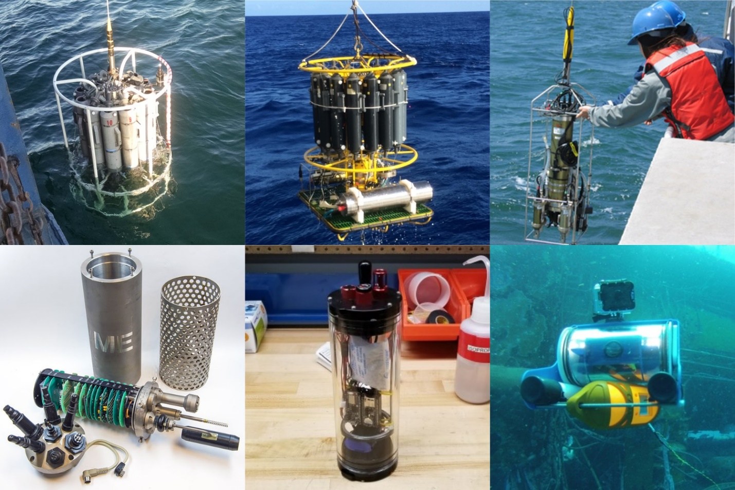
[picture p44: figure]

Figure 1. A selection of various CTDs used for field work. Top left: A CTD and rosette deployed from a NOAA boat (WHOI); top center: A CTD and rosette deployed by IFREMER; top right: a student deploys a CTD (MIT); bottom left: an 80s era ME GRISARD CTD; bottom center: the CTDizzle open-source CTD by Ian Black; bottom right: a YSI Castaway affixed to an OpenROV 2.3 (Sofar Ocean).

CTDs come in a variety of shapes, sizes, and applications. Most oceanographic research vessels have a CTD connected to a rosette platform, which houses other instruments and collects water samples in parallel with real-time data. CTDs are also commonly attached to fixed moorings, autonomous underwater vehicles (AUVs), remote-operated vehicles (ROVs), and, on occasion, marine animals (Hooker and Boyd, 2003).

Commercial CTDs are expensive, with even the most affordable models costing several thousand dollars. Many contemporary instrumentation companies now use a subscription model, locking data analysis and support behind a paywall, adding yet another cost. For near-shore oceanographic research on the continental shelf, where the water depth rarely exceeds 200 meters, this cost can be prohibitive. The expense of the CTD is a barrier-to-entry for formal and informal researchers working with limited budgets, including scientists from low- and middle-income countries and small island states, as well as citizen oceanographers, environmental educators, conservation and management practitioners, and students of all levels interested in understanding their local coasts and waterways.

Climate change, ocean acidification, and sea level rise create an urgent need for extensive measurements of oceanographic conditions both globally and locally (Stammer et al., 2016;

Stephen et al., 2016). At the same time, government funding at both state and federal levels for climate change research can be unreliable, if not wholly non-existent. This creates a pressing demand for low-cost alternatives to common scientific instruments that allow formal researchers to stretch the impact of extant funding while simultaneously enabling informal researchers (such as environmental monitoring organizations and non-governmental organizations, as well as concerned community members) to contribute water-quality measurements.

The OpenCTD is a low-cost, open-source CTD designed intentionally for budget-restricted scientists, educators, and researchers working in nearshore coastal ecosystems, where entire research projects can be conducted for less than the cost of a commercial CTD (Thaler et al., 2024). It was developed by a core team of marine ecologists in collaboration with a distributed community of scientists, engineers, makers, and conservation practitioners. It is assembled from components commonly available at large hardware stores or through major online retailers.

The OpenCTD is built by the end-user, providing both access to the tools of oceanography as well as the skills to maintain, calibrate, repair, and replace OpenCTDs. For scientists working in remote settings, where commercial maintenance solutions may be non-existent, the capacity to repair the OpenCTD in-house provides an extra buffer against equipment failure. For educators looking for novel, hands-on STEM experience for advanced students, building an OpenCTD offers an introduction to coding, 3D-printing, hardware prototyping, and electronics. Construction of an OpenCTD provides a practical foundation for courses in oceanography and marine or environmental science.

Skill Building

Though building an OpenCTD requires a variety of skills, you don’t need any background in soldering, electronics, or coding. Constructing an OpenCTD provides the foundation for developing these hardware and software skills. With a few hours of practice, you can learn the techniques necessary to build and operate your own OpenCTD.

For absolute beginners, I recommend working through Soldering is Easy: Here’s How To Do It by Mitch Altman, Andie Nordgren, and Jeff Keyzer, which is an accessible and approachable introduction to soldering fundamentals:

- Soldering is Easy: Here’s How To Do It: mightyohm.com/files/soldercomic/FullSolderComic_EN.pdf

Arduino is a coding environment built on C/C++ and designed for flexibility and ease of use, but it can seem daunting to first-time users. Practically, the OpenCTD source code is complete, and most users will only need to make small alterations to 3 lines of code during assembly and testing, but it is helpful to understand what the software is doing. Calibration and troubleshooting will require users to load different programs onto the completed OpenCTD. If you want to add new sensors, change the sampling rate, or simply alter the format for the data file, you’ll need to be comfortable making modifications to the source code.

Basic familiarity with the Arduino Integrated Development Environment (IDE) is essential. Environmental Monitoring with Arduino: Building Simple Devices to Collect Data About the World Around Us is a short, easy to understand, though dated, introduction to the Arduino ecosystem, and will provide you with many ideas for expanding your toolbox of open-source environmental sensors.

- Environmental Monitoring with Arduino: https://amzn.to/32myCR3

Project Status and Compatibility

OpenCTD is stable (as of 6/21/2023) on the ATSAMD21G18 ARM Cortex M0 processor. Construction workflow, as well as pinouts, bills of material, and operation are designed around the Adafruit Adalogger M0. Adjustments may need to be made to adapt to other M0-based microcontrollers.

An older version of OpenCTD is stable on the ATMEGA32U4 processor common to many Arduino systems. Construction workflow, as well as pinouts, bill of materials, and operation were designed around the Qduino Mini. Adjustments may need to be made to adapt to other ATMEGA32U4-based microcontrollers. This version is no longer supported, but is archived here: https://github.com/OceanographyforEveryone/OpenCTD/tree/main/Retired.

Acknowledgements.

From its inception, the OpenCTD and Oceanography for Everyone has benefitted from the support and expertise of an incredible community. Dr. Kim Martini provided exceptional guidance throughout the development process. Dr. Harold Tay provided extensive assistance in designing the OpenCTD control board, as well as general guidance during the entire development process. Kyle Worcester-Moore provided significant assistance streamlining the core OpenCTD code. J. Jacob Levenson has provided tremendous technical support and encouragement throughout the life of this project.

Hundreds of individuals have contributed to making the OpenCTD program a success. The authors would like to acknowledge Ian Black, Jeff Branson, David Lang, Eric Stackpole, Walt Holm, the OpenROV/Sofar Ocean Team, Miriam Goldstein, Alex Deghan and the Conservation X Labs Team, Cassie Stymiest of Educational Passages, the naturalists from Bar Harbor Whale Watch Company, Coastal Research & Education Society of Long Island, Boston Harbor City Cruises, Hyannis Whale Watch Cruises, Blue Ocean Society for Marine Conservation, and the college of the Atlantic, Henry Reiske and Katie Gavenus of the Center for Alaskan Coastal Studies, the students and teachers of Chapman and Homer Flex High School in Homer, Alaska, Tammy Silva and David Wiley of the Stellwagen Bank National Marine Sanctuary, Brian Marx,

Andrea Schmuttermair, Jamison Smith, Lisa Robbins, Ruth Stilwell, Allie Wilkinson, David Shiffman, and Amy Freitag.

Seed funding for the OpenCTD project was provided via a crowdfunding campaign to ADT and SKS via Rockethub. Sustaining funding for the OpenCTD was provided via an ongoing crowdfunding campaign to ADT via Patreon. The SEAoTech project was supported by a contract from the Bureau of Ocean Energy Management (140M0121D0004). Community Oceanography While Watching Whales was supported via a grant to ADT from the National Marine Sanctuaries Foundation and the Bureau of Ocean Energy Management (M17PG00019/P00002). A grant to improve the documentation for the project was provided by the Open Source Hardware Association to ADT.

## Materials, Tools, and Consumables

The approach to designing the OpenCTD focuses on accessibility—both accessibility of the components and the relative ease of construction. The goal is that any user should be able to source the parts and tools necessary to build their own OpenCTD without needing to rely on custom manufacturing or highly volatile small-batch producers. The number of non-standard parts are kept to a minimum and, when unavoidable, sourced from manufacturers with a long history of consistent quality who will continue to manufacture and support these components into the foreseeable future.

The OpenCTD can be assembled entirely from components available from large online electronics vendors such as Adafruit, Sparkfun, DigiKey, Amazon, or AliExpress as well as local hardware stores, with the exception of the OpenCTD Carrier Board. Many components can also be purchased directly through their supplier or sourced through auction sites at lower cost. Quality across suppliers for most components is generally consistent.

Some parts, such as resistors and capacitors, are cheap but hard to source individually. “Introduction to electronics"-type kits, which include many standard resistors and capacitors in small batches tend to be the most economical choice.

Raw, calibrated absolute pressure sensors are available in both 14-Bar and 30-Bar modules from several vendors. Pressure sensor breakout boards are available from a variety of manufacturers and instructions for building your own pressure sensor from principal components is provided in Appendix A.

While a Bill of Materials with recommended parts and their suppliers is provided, these are not necessarily the least expensive options and prices can vary significantly depending on local availability and the number of units being built. Part availability varies from month to month, and some components may become permanently unavailable or listed under a new manufacturer and product name. We do our best to keep the bill of materials up-to-date. If you find any discrepancies, please contact the OpenCTD team through oceanographyforeveryone.com.

When available, an Amazon Affiliate link is provided to purchase components. The OpenCTD project gets a small kickback when you buy a component through those links, which helps offset the cost of development and testing for the OpenCTD. This is, however, not an endorsement of Amazon and users are encouraged to seek out local suppliers and small businesses wherever possible.

OpenCTD Rev8 Parts Checklist

Here you will find everything you need to build an OpenCTD. We’ve broken this checklist out into each section of the manual and list each component where it appears in the build process for the first time. We have intentionally put the Bill of Materials at the end of thew manual to encourage you to read the whole document before buying parts. OpenCTD Rev8 kits are available through our online store at https://oceanographyforeveryone.bigcartel.com/.

Prepare the Adalogger M0

- Adalogger M0 (with male headers)
- MicroSD Card
- USB (micro) cable

Prepare the Carrier Board

- OpenROV Rev8 Carrier Board
- Female headers for Adalogger M0 (12-pin and 16-pin)
- Female headers for DS3231 RTC (8-pin)
- Male headers for Electrically Isolated EZO Carrier Board (5-pin)
- 2-position switch
- Female headers for MAX31865 PT1000 temperature amplifier (8-pin)
- 10 kOhm resistor (2)
- 4-pin JST header

Prepare the Real-Time Clock

- DS3231 Real-Time Clock (with male headers)
- CR1220 coin cell battery

Prepare the MAX31865 PT1000 Temperature Amplifier

- MAX31865 PT1000 temperature amplifier (with male headers)
- 3-pin JST SM connector (male)

Assemble the Control Unit

- 10mm standoff (3)
- 2.5mm nylon screws (6)
- Atlas Ezo Conductivity Circuit
- Electrically Isolated EZO Carrier Board (with metal standoffs and screws)
- 5-pin female-to-female jumper wire

Powering the OpenCTD

- 3.7v 400mAh lithium-ion battery

Prepare the PT1000 Temperature Probe

- PT1000 temperature probe
- 3-pin JST SM connector (female)
- Solder seal wire connectors (3)

Prepare the Sparkfun Pressure Sensor

- Sparkfun Pressure Sensor Breakout Board
- 20-cm long 22-gauge stranded wire (4)
- 4-pin JST connector
- Solder seal wire connectors (4)

Prepare the Atlas Conductivity Sensor

- Atlas K1.0 Conductivity Probe

3D-printing (these are the parts you will 3D print yourself)

- Sensor Baseplate
- Electronic Chassis Bottom
- Electronic Chassis Top
- Electronic Chassis Cap
- Router Jig 1
- Router Jig 2
- Test Cap Tightening Handle

Cutting the PVC Housing

- 12” schedule 40 PVC Pipe

Pot the Pressure Sensor

- 2-ton instant epoxy

Potting the OpenCTD

- E/A120-HP 2-part epoxy
- Long Taper Tip Nozzle with Bayonet Connection for Two-Part Cartridge

Final Preparation and First Deployment

- 2” hose clamp (2)
- Short length of Polypro rope (2)
- 2” plumbers test cap

Calibration

- K 1.0 Calibration Standard

Tools and Consumables

A basic soldering kit is sufficient for assembly. Several components require a 3D printer.

Tools for general electronics work: flush cutters, wire strippers, soldering iron, solder tip cleaner, helping hands, needle-nosed pliers, utility knife, heat gun, precision screwdrivers. Consumables for general electronics work: lead-free solder, electrical tape.

Tools for 3D printing: 3D printer, deburring tool or utility knife.
Consumables for 3D printing: PLA Filament.

Tools for housing and adhesion: Hand saw or PVC pipe cutter, drill with 1” bit or router and jig, Epoxy gun for 50ml cartridges.
Consumables for housing and adhesion: sandpaper.

Tools for Arduino programming: Computer capable of running Arduino IDE.

Andrew’s Toolkit

Sometimes it is nice to have a list of tried and tested tools rather sourcing everything yourself.

The following are the tools in Andrew Thaler’s personal OpenCTD toolkit and his preferred consumables. Though these may not represent the best tools for your needs, this kit has been used to reliably develop and construct hundred of OpenCTDs at workshops around the world.

A note on Epoxies and Glues:

We recommend Loctite Hysol E-120HP. Epoxies with similar characteristics may be acceptable replacements. We have tested several different epoxies and glues to ensure a generally wide variety of options for sourcing. For smaller applications, such as potting the pressure sensor, we use a standard 5-minute marine epoxy.

Hysol EA-90FL and EA E-120HP have been extensively tested in OpenCTDs as well as in other marine hardware, however it is not always easy to source. Other two-part epoxies can also be used for building the sensor pass-though, provided they have a minimum sheer strength of 900 PSI and a medium viscosity rating. Tests with Hysol E-60HP resulted in consistent failures and E-60HP as well as epoxies with similar characteristics, particularly those with high viscosity, should be avoided.

Any 5-minute marine-grade epoxy is acceptable for sealing the pressure sensor.

Since Andrew runs a fabrication studio involved in multiple projects, in several cases these tools may be excessive.

Soldering Irons (Yes, he has three irons, each of which is useful in different circumstances. Any of them can be used to complete the entire assembly. The PINECIL is the best soldering iron for most applications):

- For benchtop work with reliable power: Hakko FX888D-23BY Digital Soldering Station (https://amzn.to/3vCWNuj)
- For field work with limited power access: Hakko FX-901/P Cordless Soldering Iron (https://amzn.to/30Uz62r)
- For workshops, small spaces, or where USB-C power supplies are preferable: PINECIL – Smart Mini Portable Soldering Iron (https://pine64.com/product/pinecil-smart-mini-portable-soldering-iron/). (https://pine64.com/product/pinecil-smart-mini-portable-soldering-iron/) Requires a high wattage USB power supply like this one: Anker Nano USB C Charger (https://amzn.to/4oIBm7d).
- Solder Tip Cleaner: Hakko 599B-02 Wire-type soldering iron tip cleaner (https://amzn.to/38RF08S)
- Helping Hands: KOTTO Helping Hands Soldering Stand (https://amzn.to/38PSeD6)

Hand Tools (for both electronics and housing assembly):

- Flush cut pliers: 170-II Micro-Shear Flush Cutter (https://amzn.to/3bYQPMp)
- Wire strippers: Stanley Hand Tools 84-213 Wire Stripper (https://amzn.to/30URW9D)
- Needle-nosed pliers: Stanley 84-096 5-Inch Needle Nose Plier (https://amzn.to/3eS8cAD)
- Utility knife: OLFA 1075449 XA-1 9mm Fiberglass Rubber Grip Utility Knife (https://amzn.to/3cOIxpw)
- Epoxy gun: 3M 08190 Performance Manual Applicator for 50 ml Cartridges (https://amzn.to/3twpOWG) Note: when Andrew bought this applicator, it was still under patent and the only version available. It’s worked reliably for 10+ years, but there are now several much less expensive clones on the market that all look perfectly fine.

Power Tools (these are all overpowered for the job, but are common in most machine shops, maker spaces, and maintenance facilities and will make housing assembly faster and more consistent):

- Drill: DEWALT 20V MAX Cordless Drill / Driver (https://amzn.to/2Qajoy0)
- 1-inch spade bit: Irwin Tools 1764345 Short Spade Bit 1" (https://amzn.to/3tuSdwn)
- Router: PORTER-CABLE 690Lr Router 1-3/4Hp (https://amzn.to/3eNjAO6)
- Milwaukee M12 12-Volt Cordless PVC Shear: (https://amzn.to/44eDxFG) If you’re planning on making several dozen OpenCTDs, this pipe shear, while expensive, will save you significant time and reduce PVC waste.

- Chop saw: The sliding compound miter saw Andrew uses is no longer in production, but pretty much any standard chop/miter saw will do and, in a pinch, a handsaw works just fine.

3D Printing (Pretty much any 3D printer will work, however, Andrew conducted a review of low-cost printers to determine the best 3D printer for field work, using the OpenCTD parts as one of the test standards. You may find the results of that project helpful in determining the best printer for you: http://www.southernfriedscience.com/the-quest-for-the-best-tough-3d-printer-for-under-200-our-final-recommendations/): (http://www.southernfriedscience.com/the-quest-for-the-best-tough-3d-printer-for-under-200-our-final-recommendations/)

- 3D Printer: Creality Ender-3 3D Printer (https://amzn.to/2QdtIFr)
- Deburring tool: General Tools 484 Swivel Head Deburring Tool Kit (https://amzn.to/3eThJY8)

Programming:

- Computer: Any modern PC, Mac, or Chromebook can run the Arduino IDE. For users who may not be able to install software on their computer, Arduino also provides a web-based IDE.

Consumables:

- PLA Filament: PolyTerra™ PLA (https://us.polymaker.com/products/polyterra-pla)
- Lead-free solder: Lead Free Solder Wire (https://amzn.to/4oCo63K)
- Electrical tape: 3M Scotch #35 Electrical Tape (https://amzn.to/2QeA9rS)
- 22-gauge silicone wire: 22 Gauge Silicone Wire Kit (https://amzn.to/3CN0F0z)
- Sandpaper: 3M Garnet Sandpaper, 9-Inch by 11-Inch, Assorted-Grit (https://amzn.to/3vCfaQ9)
- 2-part adhesive epoxy: Loctite E-120FL Hysol Epoxy (https://amzn.to/315kQ6V)
- Five-minute epoxy: Loctite Epoxy Five Minute Instant Mix (https://amzn.to/3tuKM8q)

## Safety

“There is no more important rule than to wear safety glasses.”

Norm Abrams

There are only a few potential hazards while working on the OpenCTD. Soldering involves both a hot soldering iron and fumes produced from burning solder. Potting the sensors involves the use of a 2-part chemical epoxy which can bond with skin. Trimming wires may produce small metal projectiles which can damage the eye. Working near water presents a drowning risk. All of these hazards can be mitigated with basic safety protocols and proper protective equipment.

What tools will I encounter?

Construction of the OpenCTD requires only basic hand tools, as well as electronic tools associated with soldering. If you are constructing a PVC housing, you might also use power tools, including a miter saw, a jig saw, a drill, a PVC cutter, or a router. For workshops with primary school students, we recommend that the instructor prepare the PVC housing in advance, as this process is messy, requires the use of power tools, and adds additional time to the build process.

Whenever you are working with tools, you should wear safety glasses to protect your eyes. When working with power tools, what you aren’t wearing is as important as what you are wearing. Avoid gloves or neckties, as well as anything with long cords, especially hoodies with drawstrings. These cords can become trapped in the tool and pull the user towards a spinning blade.

When soldering, be aware that the iron is extremely hot. Contact with a soldering iron will result in immediate 2nd degree burns. Only hold the soldering iron by the insulated grip and stow it in a secure soldering iron holder. Never leave a hot iron unattended. Always turn off and unplug the iron when not in use. Whenever hot irons are in use, other participants should take extra care not to jostle the table or the person holding the iron and avoid any distractions. Safety glasses should be worn when soldering.

The heat gun used for melting heat shrink tubing can also get very hot. Be aware of its location and never touch the exposed metal portion.

Soldering produces fumes. We recommend using a lead-free solder to dramatically reduce the presence of harmful fumes. In a well-ventilated environment using lead-free solder, the fumes produced from soldering should pose no health hazard. However, for added safety, a small fume extractor can be used to draw the fumes away from your person.

When trimming pins on the control board or other components, the snipped ends tend to fly off. This can be avoided by placing a finger over the end about the be snipped to prevent it from launching into the air. Some high-end flush cutters have a small magnet to prevent fly aways. When trimming pins, wear safety glasses and be aware of who is around you.

What chemicals will I encounter?

The OpenCTD is potted using two different kinds of 2-stage epoxy. The epoxy used to seal the pressure sensor into the baseplate is an off-the-shelf 2-ton epoxy commonly found in hardware stores. The high-strength epoxy used to seal the sensors into the housing is a specialized epoxy available from most major adhesives distributors. Both epoxies are safe when handled properly. Always wear safety gloves and safety glasses when handling epoxy. Read the warning labels on the packaging before use. If epoxy gets on your skin or clothes, immediately flush with warm water.

General Safety

You will use sharp tools during the build process. Always be aware of any blades or cutting implements and store them appropriately. Pliers and flush cutters can pinch and break the skin. Always treat your tools with respect.

When working on the water, wear a US Coast Guard (or other relevant agency) approved life jacket.

Lithium Polymer Batteries

The lithium polymer pouch batteries used in the OpenCTD are generally safe and stable when stored and handled appropriately. In the event that a battery is punctured by a tool or inadvertently heated to extreme temperatures by a soldering iron, remove the battery from the classroom immediately and place outside on a concrete surface or fire-resistant container. The battery cannot be recovered and must be disposed of appropriately.

## Electronics

The control unit is the brain of the OpenCTD. At its core is an Adalogger M0, an SAMD-based microcontroller with a built in SD card reader. When paired with a Real-Time Clock (RTC), this will allow the user to log timestamped data that can be extracted by any microSD card reader. The Adalogger M0 is connected to a conductivity circuit and temperature amplifier through the custom carrier board.

Before beginning, familiarize yourself with the electrical components as well as the Arduino Integrated Development Environment (IDE). By ensuring that the software is running and the base components have been assembled and tested, you can save yourself significant frustration down the road. Setting up Arduino from scratch can be a challenging and unintuitive process the first time you do it, so it is a good idea to invest an hour or two into making sure you have compatible, up-to-date libraries and that the OpenCTD code compiles on your computer.

Arduino provides an online development environment if you cannot install software on your personal computer: https://create.arduino.cc/.

Adalogger M0 Software and Libraries

The Adafruit M0 Adalogger acts as both the main computer for the OpenCTD and writes data to the onboard SD Card drive. Before you begin soldering hardware, flash the software to the Adalogger M0 to confirm that the microcontroller is functioning and your Arduino IDE is set-up correctly. Ensuring that the microcontroller works with the OpenCTD firmware first will dramatically simplify any troubleshooting, later.

To prepare your computer to talk to the M0 Adalogger, download and install Arduino IDE (https://www.arduino.cc/en/Main/Software). You will need to install additional boards so that Arduino IDE will be able to recognize the Adalogger. For a detailed walkthrough of this process, with screenshots included, please visit: https://learn.adafruit.com/adafruit-feather-m0-adalogger/setup. (https://learn.adafruit.com/adafruit-feather-m0-adalogger/setup) Please be aware that the Arduino, Adafruit, and GitHub Software may have been updated more recently than this manual and that the location of certain tools and functions may differ from the instructions.

All OpenCTD software and documentation are hosted on GitHub. GitHub can seem daunting to new users. At its core, GitHub is a tool to organize and coordinate files and maintain version control (multiple people can edit the same file, while keeping everything in sync). Projects are organized into repositories (‘repos’) that contain the source code, supporting documents, data files, and other materials needed for each project. When you visit a repo, check the README.md, this will generally describe the project (including the current status), contain necessary guides, and let you know how to contribute.

1. Launch Arduino IDE.

2. Under preferences, in the File menu (on Apple Computers, this in under the Arduino menu), add the following URL to the “Additional Boards Manager URLs” field:
https://adafruit.github.io/arduino-board-index/package_adafruit_index.json
3. Click “Ok” and then navigate to Tools > Board > Boards Manager.
4. In Boards Manager, search for “Adafruit SAMD Boards” and install the library. Now search for “Arduino SAMD Boards” and install this library as well. This may take a while.
5. Restart Arduino IDE.
6. Install the required libraries listed below (Sketch > Include Library > Add .ZIP Library) and update Arduino IDE as needed.
7. Restart Arduino IDE.

Required Arduino Libraries

The following Arduino libraries are required for the OpenCTD Rev8 and come packaged with Arduino IDE by default:

Wire. For communicating with I2C devices like the pressure sensor.
SPI. Serial Peripheral Interface for communicating with a standard SD card reader. SD. For reading and writing to a standard SD card reader.

You will need to download and install the remaining libraries manually. Please refer to https://www.arduino.cc/en/Guide/Libraries for detailed instructions for installing libraries.

MS5803_14. For the MS5803 14-Bar pressure sensor.
Adafruit_MAX31865.h. Allows you to communicate with the PT1000 temperature amplifier and probe.
RTClib. For controlling and reading the Real-time Clock
SoftwareSerial. A modified version of the standard serial monitoring program that works with SAMD microcontrollers like the Adafruit Feather M0.

These libraries can be downloaded as compressed .zip files from the OpenCTD GitHub Repository:

https://github.com/OceanographyforEveryone/OpenCTD/tree/main/Software/Support

Flash the OpenCTD software to the Adalogger

Install the OpenCTD software on the Adafruit Adalogger M0. On some Adaloggers, Adafruit ships the microcontroller preloaded with both Arduino and Circuit Python, with Circuit Python being the default. When you plug your Adalogger in for the first time, it will open into the Circuit Python boot drive. You can ignore this. After you flash the OpenCTD software, the Adalogger will default to Arduino.

1. Restart Arduino IDE. You should see several new Adafruit options in the Board menu. The Adalogger is an Adafruit Feather M0 with an embedded SD card reader.
2. Select “Adafruit Feather M0” from the Board menu.
3. Connect your Adalogger to your laptop using a micro-USB cable. The necessary drivers should automatically install.
4. Open the OpenCTD_M0_R8.ino source code in Arduino IDE.
5. Under Tools > Port, select the COM port that reads “Adafruit Feather M0” (it should autodetect, but doesn’t always).
6. Click Upload (either the right pointing arrow on the main interface or under
Sketch > Upload). The code will compile and upload to the Adalogger.

Once the OpenCTD firmware is flashed to the Adalogger M0, use the serial monitor in Arduino IDE to verify that it is working correctly. With the Adalogger connected to your computer via USB, open the Serial Monitor by clicking the magnifying glass in the upper righthand corner of Arduino IDE or through Tools > Serial Monitor. The software will initialize the SD card reader.

The serial monitor should say “Card failed, or not present”. Insert an SD card. The Adalogger will initialize and then attempt to read the Real-Time Clock and sensors, which will fail. Unplug the control unit, remove the SD card, and confirm via SD card reader that an empty file was created on the SD card.

Prepare the Adalogger M0

The Adalogger M0 needs headers. Headers are the male or female pin assemblies that allow you to connect and disconnect electronic components from a PCB. Headers make come pre-cut or in long strips that need to be cut to length to align with the correct pins on the carrier board. A “pin” refers to any electrical contact point and will generally be used in this guide to refer to the holes in circuit boards through which wires, headers, and other components will be soldered.

When placing headers for soldering, the short pins go through the holes in the printed circuit board and are soldered on the opposite side.

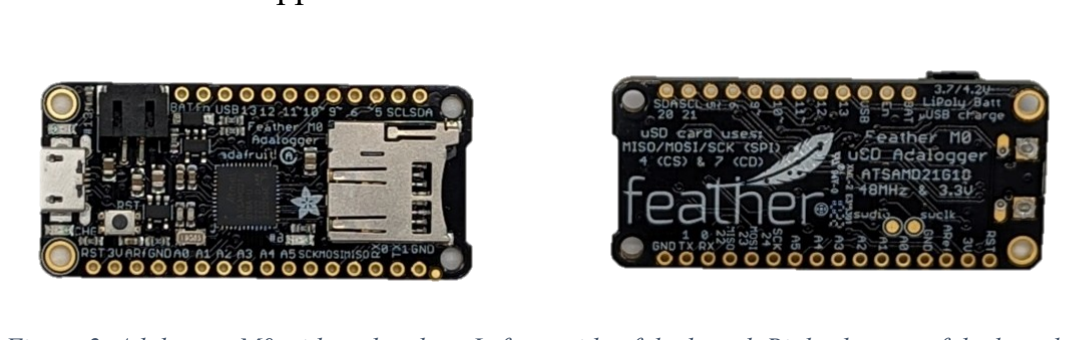
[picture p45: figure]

Figure 2. Adalogger M0 without headers. Left: topside of the board. Right: bottom of the board.

1. Slot male headers into the through-holes on the underside of the Adalogger M0, ensuring that the number of headers matches the number of available pins (16 on one side, 12 on the other). The long header pins should point down. If you are using generic headers, cut them to length with flush cutters so that the number of posts matches the number of pins on each side.
2. Confirm that the headers are straight and perpendicular to the face of the Adalogger.
3. On the top of the Adalogger, solder the four corner pins, double check that the headers are straight, and then solder the remaining pins.
4. Using the flush cutters to clean up any protruding solder joints.
5. Insert a microSD card into the SD card reader.

Figure 3: Adafruit M0 Adalogger with male headers (SD card not shown).

Prepare the Carrier Board

The carrier board allows for rapid and accurate assembly of the OpenCTD control unit. Your carrier board should be labeled OpenCTD rev8. The color of the board may vary. Some early boards may be labeled “OpenCTD 8x”.

Figure 4: OpenCTD Carrier Board. Topside of the board above, underside of board below.

1. Slot female headers on the topside of the carrier board in the pins in the box labeled Adalogger. You may need to trim the strip of female headers down to size using flush cutters so that the number of posts match the number of pins
in the carrier board.
2. Solder female headers for the Adalogger M0 to the carrier board, starting with the four corners to hold them in place.
3. Slot female headers on the underside of the carrier board in in the box labeled DS3231 and solder them into place.
4. Slot male headers for the Atlas Electrically Isolated EZO Carrier Board on the underside of the carrier board in the box labeled J5 and solder them into place.

5. Slot the 2-position switch on the topside of the carrier board in the box labeled J1 and solder them into place. The pins will be extra long and need to be trimmed.
6. Slot female headers for the MAX31865 temperature amplifier on the topside of the carrier board in the box labeled J4 and solder them into place.
7. Solder 2 10kOhm resistors into the slots on the topside of the carrier board reserved for resistors inside the box labeled MAX31865. The pins will be extra long and need to be trimmed. The resistors are bidirectional and orientation does not matter.
8. Slot the 4 pin JST connectors on the topside of the carrier board in the box labeled J3 and solder into place.

### 9. Optional Step: To use the two moisture sensors embedded in the control

board, lightly solder to small blobs onto each of the four pads labeled Moisture Cutoff, making sure the two adject pads do not connect. This will cause the device to power down if the pads are short-circuited by seawater, hopefully preserving the electronics in even of a housing failure.

10. Using the flush cutters, snip down any protruding pins so that they sit flush with the solder joint.

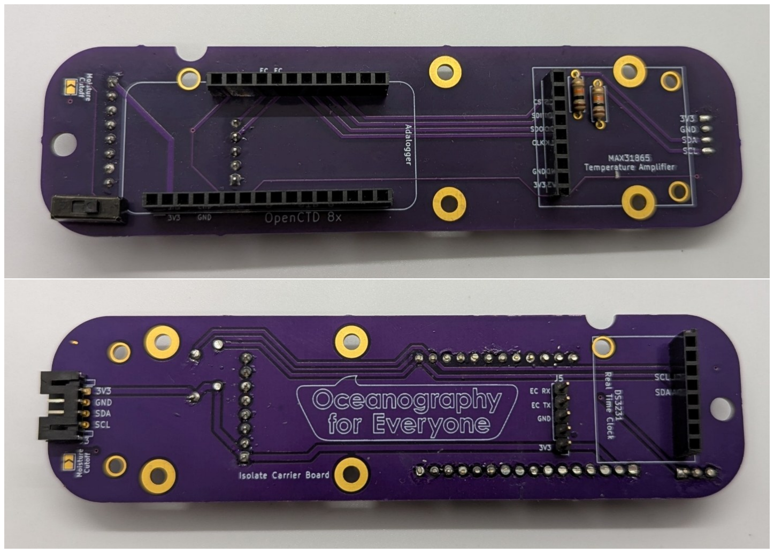
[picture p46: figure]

Figure 5: Fully populated OpenCTD control board. Topside of the board above, underside of board below

Prepare the Real-Time Clock

The Real-Time Clock (RTC) sets its time based on the time displayed on the computer when the code is compiled. Should the RTC ever lose time, you can use the program RTC_Reset in the OpenCTD GitHub repository under Support to reset the clock to the system time on a connected PC. Make sure you have the orientation of the pins correct before soldering or you’re going to have a bad time!

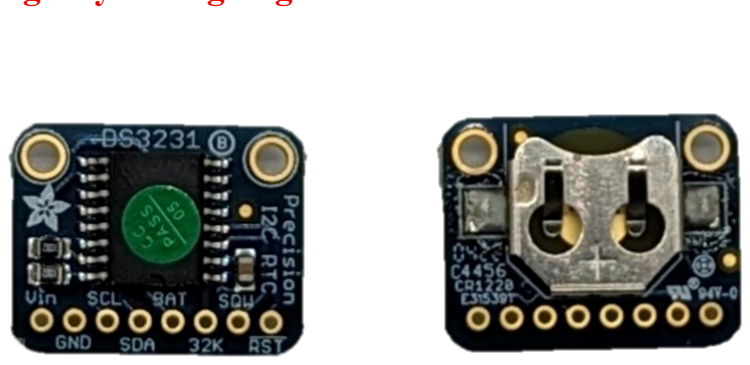
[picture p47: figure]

Figure 6. Real-Time Clock module without headers. Left: chip side of the board. Right: battery side of the board.

1. Slot the male header pins into the RTC module on the chip side of the board such that the battery is facing up and the header pins extend from the opposite side of the module. Do not solder with the battery installed in the RTC.
2. Solder the male header pins into the RTC module.
3. Using the flush cutters, snip down any protruding pins so that they sit flush with the solder joint.
4. Insert the CR1220 battery into the RTC, positive side facing out.

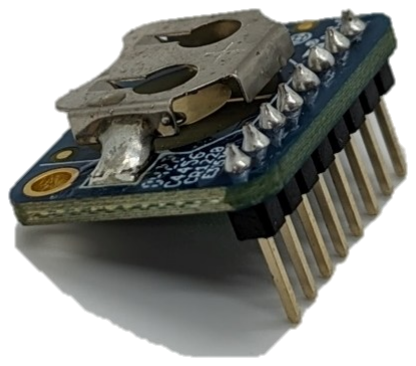
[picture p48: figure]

Figure 7.Real-Time Clock module with male headers soldered to the chip side of the board.

Prepare the MAX31865 PT1000 Temperature Amplifier

The PT1000 resistance temperature detector (RTD) amplifier is designed to read the low resistance of a platinum temperature resistor. This MAX31865 amplifier can read 2-, 3-, or 4-wire sensors. For the OpenCTD, we use a 3-wire platinum temperature sensor. You will have to set the amplifier to 3-wire by soldering two pads and breaking one jump pad, as described in the Adafruit instructions for 3-wire sensors here: https://learn.adafruit.com/adafruit-max31865-rtd-pt100-amplifier/rtd-wiring-config (https://learn.adafruit.com/adafruit-max31865-rtd-pt100-amplifier/rtd-wiring-config) or in steps 1 – 3, below. Please note, the temperature amplifier will be mounted upside-down on the control board, and the header pins will point up from the same side as the screw-block terminals. Make sure you have the orientation of the pins correct before soldering or you’re going to have a bad time!

1. Locate the pads labeled 2/3 Wire and 24 3 on your MAX31865 amplifier.
2. Using a utility knife, break the small copper trace connecting the rectangular pads labeled 2 and 4. By carefully applying a small blob of solder, connect the middle rectangular pad labeled 4 to the rectangular pad labeled 3.

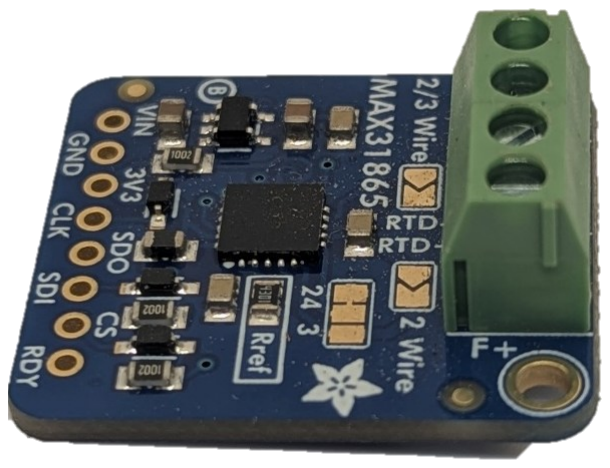
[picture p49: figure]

Figure 8. MAX31865 amplifier for PT1000 resistance temperature detector (RTD), as it arrives from the manufacturer.

3. By carefully applying a small blob of solder, connect the triangular pad
labeled 2/3 wire to the chevron-shaped pad, also labeled 2/3 Wire. By creating these connections, you are telling the amplifier to look for 3 wires coming from the temperature probe.
4. Solder the male headers so that the long pins are pointing up, on the same side as the large screw terminals.

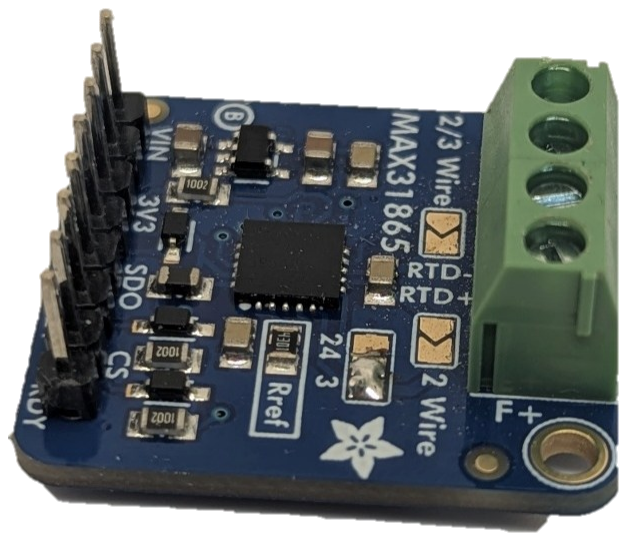
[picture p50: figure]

Figure 9. MAX31865 amplifier with pads 2 and 4 connected and the male headers installed. Note: pads labeled 2/3 Wire are not connected in this image.

5. Insert the male side of the 3-pin connector cable into the screw terminals labeled F+, RTD+, and RTD-. Tighten the screw terminals so that the bare wires make contact with the metal pad inside the screw terminals and do not pull out with a light tug. If necessary, you can shorten the wires on the 3-pin connector cable.

Figure 10. Completed MAX31865 amplifier with 3-pin connector cable installed.

Assemble the Control Unit

You will not need to solder anything during this section.

1. Slot the RTC into the RTC headers on the underside of the carrier board and ensure that the RTC board is parallel with the carrier board. Secure the RTC to the board using the 10mm standoff and 2.5mm nylon screws.
2. Insert the Atlas Ezo Conductivity Circuit into the headers on the Electrically Isolated EZO Carrier Board. The pins labeled PRB and VCC should face towards the BNC connector. Using the metal standoffs provided, mount the EZO Carrier Board to the OpenCTD Control Board upside down, so that the EZO conductivity circuit is sandwiched between the two boards. You may need to use the flush cutters to trim down any sharp pins which might press against the EZO Conductivity Circuit.
3. Use the included 5-pin female-to-female jumper wire to connect the headers on the Electrically Isolated EZO Carrier Board to the headers labeled J5 on the OpenCTD Carrier Board, making sure that you match the header labels for each pin.
4. Slot the Adalogger M0 on top of the custom carrier board by lining up the male, downward-facing header pins on the Adalogger with the female, upward facing header pins on the carrier board.

5. Slot the MAX31865 amplifier into the MAX31865 amplifier headers on the topside of the carrier board and ensure that the MAX31865 amplifier board is parallel with the carrier board. Secure the MAX31865 amplifier to the board using 2 10mm standoffs and 2.5mm nylon screws. This board should also be upside down.

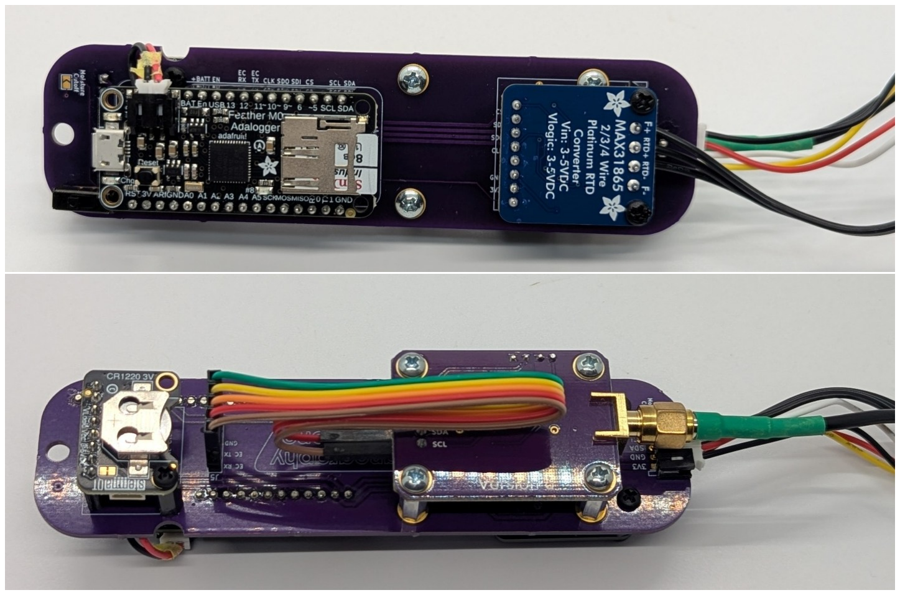
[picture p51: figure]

Figure 11. Topside and underside of completed OpenCTD Rev8 Control Unit.

Powering the OpenCTD

The Adalogger has an internal 100mA charging unit, which means a standard 400mAh battery will take 4 hours to charge. Using an external lithium polymer battery charger with higher amperage can dramatically speed up the charging process. For charging, we use this 500-mA charger (https://www.adafruit.com/product/1904) which cuts the charging time on a 400mAh battery down from 4 hours to less than 1 hour.

1. Plug in the battery and ensure that the switch functions correctly.
2. The 3.7v 400mAh is ideal for the OpenCTD. It fits snugly between the carrier board and the Adalogger M0 and lasts for roughly 18 hours of continuous use. If you need more power, larger batteries that use a JST connector can be used. Make sure that the positive and negative leads on batteries from other supplier correspond to the positive and negative terminals on the Adalogger M0. There is a small notch in the carrier board that allows a larger battery to mounted to the underside of the carrier board or anywhere else within the housing.

Note: Depending on the amperage of the USB power supply that you’re connected to, there may not be enough power to drive the EZO EC chip from USB power. You may also need to plug the battery into the 2-pin battery JST connector.

If the EZO conductivity circuit blinks red, it is not receiving enough power.

Prepare the PT1000 Temperature Probe

The PT1000 temperature probe connects to the 3-pin connector that you installed on the MAX31865 amplifier.

1. Remove the spade terminals and strip ¼ cm off the end of each of the three wires.
2. Solder the female end of the 3-pin lead to the exposed wires, either using solder shrink tubing or solder and heat shrink. Make sure that the two red wires correspond to the pin labeled F+ and RTD+, and the clear wire aligns with the pin labeled RDT-.
3. Plug the temperature probe into the MAX31865 amplifier.

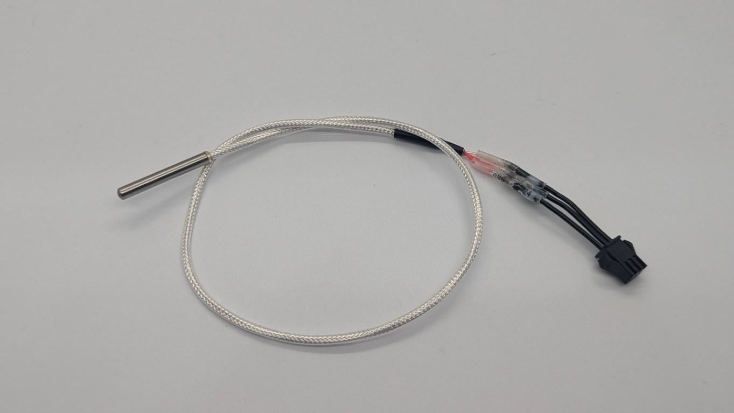
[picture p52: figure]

Figure 12. PT1000 Temperate Probe.

Prepare the Sparkfun Pressure Sensor

Please note: An alternative to the Sparkfun Pressure Sensor Breakout Board is available from Oceanography for Everyone, however, it requires surface mounted soldering and may be difficult for inexperienced builders. See Appendix A.

For the Sparkfun Pressure Sensor Breakout Board:

1. Strip ½ cm off the end of 4 different colored 20-cm lengths of 22-gauge stranded wire. We recommend red for VCC; black for GND; yellow for SCL; and white for SDA.
2. Solder those wires to the GND, 3.3v (or VCC), SDA, and SCL pins on the back of the Sparkfun Pressure Sensor Breakout Board. Keep track of which wire goes to which pin. Note that the wires must extend from the side opposite the pressure sensor.

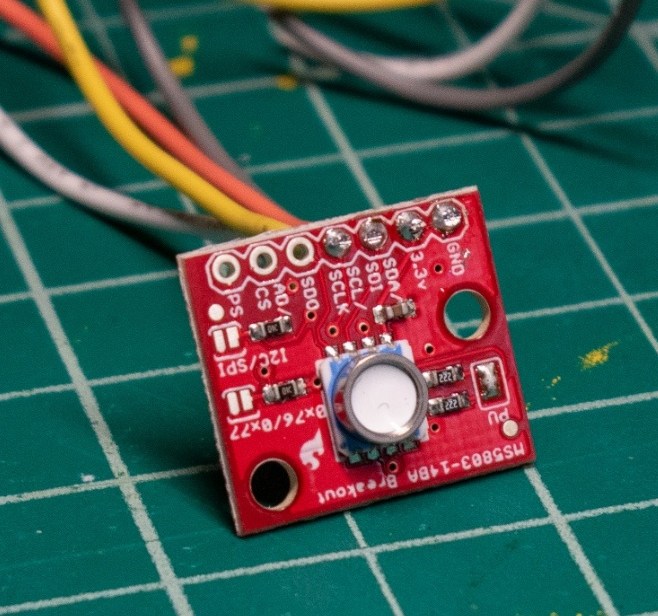
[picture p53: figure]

Figure 13. Sparkfun Pressure Sensor Breakout with soldered pins.

3. Solder the female end of the 4-pin JST connector to the exposed wires, either using solder shrink tubing or solder and heat shrink. Make sure that the wires from the breakout board correspond to the labels on the carrier board.
4. Connect the 4-wire JST connector to the 4-wire JST headers on the carrier board.

Prepare the Atlas Conductivity Probe

The Atlas Scientific conductivity probe comes in both long and short varieties, with paired leads that terminate at a large BNC connector. You will not need to cut or modify this probe in any way.

1. Plug the BNC connector into the BNC threaded header on the Electrically Isolated EZO Carrier Board

While you can cut this wire to size for ease of use, Atlas Scientific advises customers to test their conductivity probe before cutting any wire, as cutting the wire will void the warranty. Atlas also provides a much more detailed step-by-step guide to cleanly and accurately cutting the conductivity sensor wire here: https://files.atlas-scientific.com/how-to-properly-cut-probe-cables.pdf (https://files.atlas-scientific.com/how-to-properly-cut-probe-cables.pdf)

If you do not have access to a coax cable stripper tool, you can carefully strip these cable using your flush cutters. It helps to cut them long and use the extra tail for practice before cutting to final length. Atlas also advise to clean any soldered leads in isopropyl alcohol to remove any flux residue which may cause resistance in the system.

Test All Components

With all the components connected to you control board, it’s time to test your soldering skills. Connect your control board to your computer using a USB cable, open Arduino IDE, and turn on the OpenCTD. Select the correct board and open the serial monitor. You should see a data stream that looks like this:

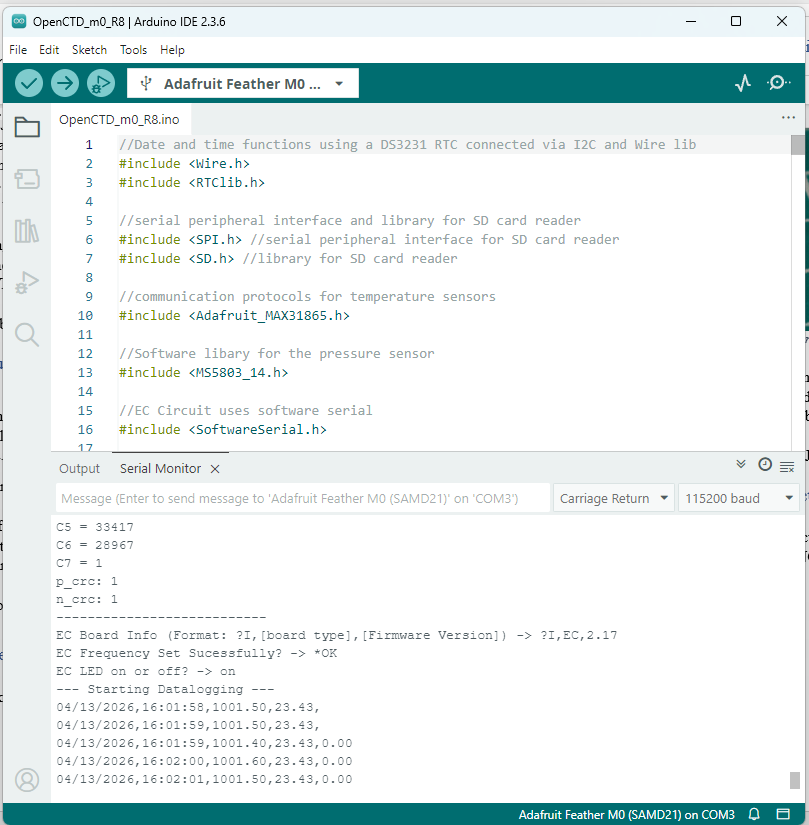
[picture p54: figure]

Figure 14. Arduino IDE and Serial Monitor readout of functioning OpenCTD.

After the bootup and diagnostic information, you should see a continuously updating line of numbers. These values are, from left to right, the date (in MM/DD/YYY format), The time (in HH:MM:SS), the pressure (mbar), temperature (oC), and conductivity (mS). Outside of the water, at sea level, in a comfortable room, Pressure should read around 1012 mbar, temperature around 21oC, and conductivity at 0 mS.

Congratulations! If everything looks normal, you’re CTD is working! If not, double check all your solder connections, make sure the wires have good contact, and check that nothing is reversed.

Now all you have to do is make you OpenCTD waterproof!

## Housing

3D-printing

It may seem counterintuitive to rely on a technology like 3D-printing in designing a low-cost and accessible oceanographic instrument but 3D-printing has matured to the point where the most affordable and widely available printers are more than sufficient for the production of these parts. This technology dramatically reduces the cost for manufacturing small and bespoke plastic components. 3D-printing plays a central role in the conservation technology movement.

The main chassis of the OpenCTD, which protects the control unit, and the sensor baseplate, which aligns the sensors and creates a bulkhead for the sensor passthrough, are 3D-printable objects. While it is possible to construct a fully functional OpenCTD without these parts, they are designed to make building and operating the device simpler and more intuitive.

- The Sensor Baseplate provides a foundation and template for arranging the sensors prior to potting in epoxy.
- The Electronics Chassis holds the Adalogger and other electronic components, allowing users to easily access the SD card while minimizing strain on the wiring and protecting and isolating the battery. The chassis is printed in three parts which fit snugly together and are held in place with electrical tape.
- The Router Jig is a set of jigs designed to fit inside a clean PVC pipe that allow you to cut 3 clean, consistent notches on the bottom of the CTD to protect the sensors while allowing water to flow through.
- The Cap Wrench is a small wrench that fits over the wingnut of the Plumber’s Test Cap, making it easier to tighten and loosen.

All parts are designed to be printed in PLA at 200-micron resolution with 50% to 100% infill. We recommend PLA over other plastics as it is Generally Regarded As Safe, theoretically compostable (but only in a commercial composter), and has not been shown to be harmful to the marine environment. ABS, in contrast, has been shown to cause developmental abnormalities in fish exposed to ABS particulates (Oskui et al., 2016). Other materials, like PETG and Nylon may be preferable but require more experience and a more advanced printer.

Andrew’s personal preference is for Polymaker Panchroma PLA, which has been optimized for strength and compostability.

- Panchroma™ PLA (https://shop.polymaker.com/)

All 3D printer files are available in the OpenCTD GitHub repository: https://github.com/OceanographyforEveryone/OpenCTD/tree/main/Hardware/3DPrints

Once the sensor baseplate is printed, use a deburring tool or some sandpaper to round off all the edges on both top and bottom as well as inside of each hole. Test fit each sensor. Sensors, especially the pressure sensor, should fit snuggly inside of their respective hole and the entire baseplate should fit tightly into a 2” PVC pipe.

The electronics chassis can be printed without supports. Test fit the two halves of the main body to ensure that they slot together firmly. Test fit the cap of the electronics chassis to ensure that it fits snugly.

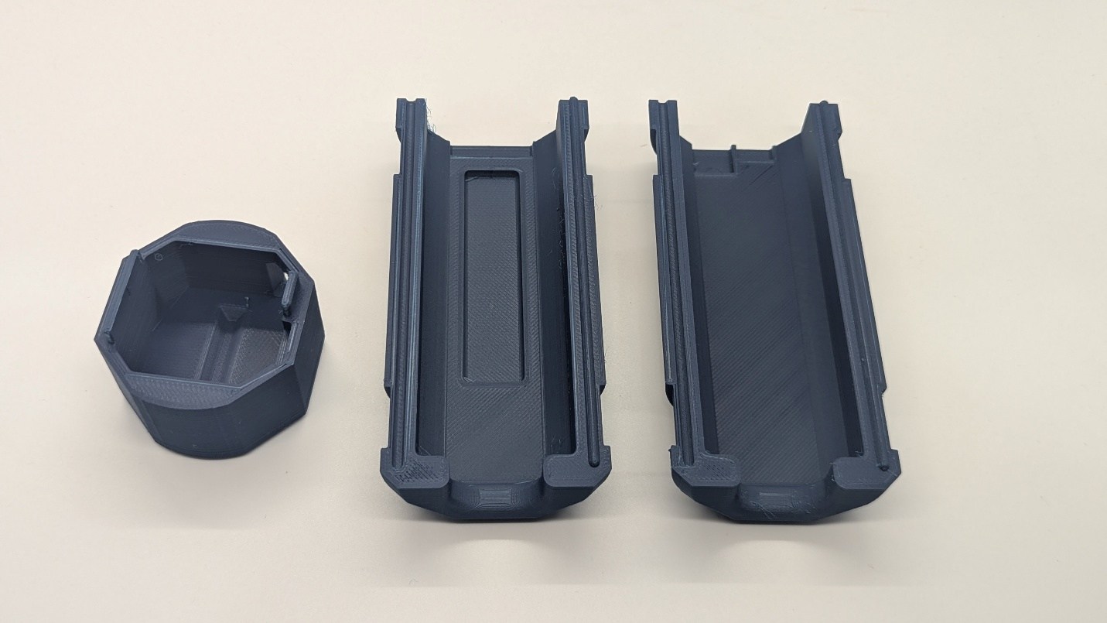
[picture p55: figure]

Figure 15: 3D-Printed chassis for OpenCTD.

Assemble the PowerSquid

PowerSquid is our name for the OpenCTD Rev8 control unit once it is housed in its protective chassis. The chassis comes in three parts, two long body pieces and one cap. This chassis will protect the control unit from drips, bumps, and knocks, but not from full submersion in seawater. A small notch in the cap allows you to access the power switch to turn the OpenCTD on and off.

1. Reconnect all cables leading to the sensor package.

2. Fold the extra wiring from the Atlas EZO Carrier Board and place the control unit in the bottom chassis piece so that the excess cable rest in the long, rectangular slot. The sensors should exit from the end with the large oval hole.
3. Place the top chassis piece on top of the control unit, making sure that the edges align. Use electrical tape or rubber bands to secure the two pieces.
4. Place the cap on the open end of the chassis assembly. It should fit snugly and remain in place.
5. Turn on the OpenCTD and confirm that it is reading all sensors.

Cutting the PVC Housing

The OpenCTD housing is comprised of a single piece of schedule-40 2” PVC pipe. Notches or holes cut in the bottom allow water to flow over the sensors while protecting them from impacts and entanglement. The sensor end will be sealed with high sheer-strength epoxy, allowing sensors to pass through the housing while preventing water from entering and damaging the electronics. The open end is sealed with an off-the-shelf pressure test cap designed for plumbers. When cutting and preparing the PVC, take care not to damage the inner surface where the test cap O-ring will seat against the PVC wall. (Note: because US-based plumbing supplies are generally measured in Imperial units, where off-the-shelf parts are used, we will use the measurement standard provided by the manufacturer.)

Using the router jig

The router jigs are designed to be used with a c-clamp and small bench router. We do not recommend attempting to route the housing notches freehand. We recommend using a ¼” compression cut template bit.

Figure 16. Bench router with PVC pipes and router jig.

1. Cut a 12” section of PVC pipe. Deburr the edges around each cut with a knife, sandpaper, or deburring tool.
2. Insert the router jig labeled RouterJigForHousing1.3mf into one end of the clean and evenly cut PVC pipe. Secure with a c-clamp. Make sure that c-clamp doesn’t come in contact with the router bit during routing.

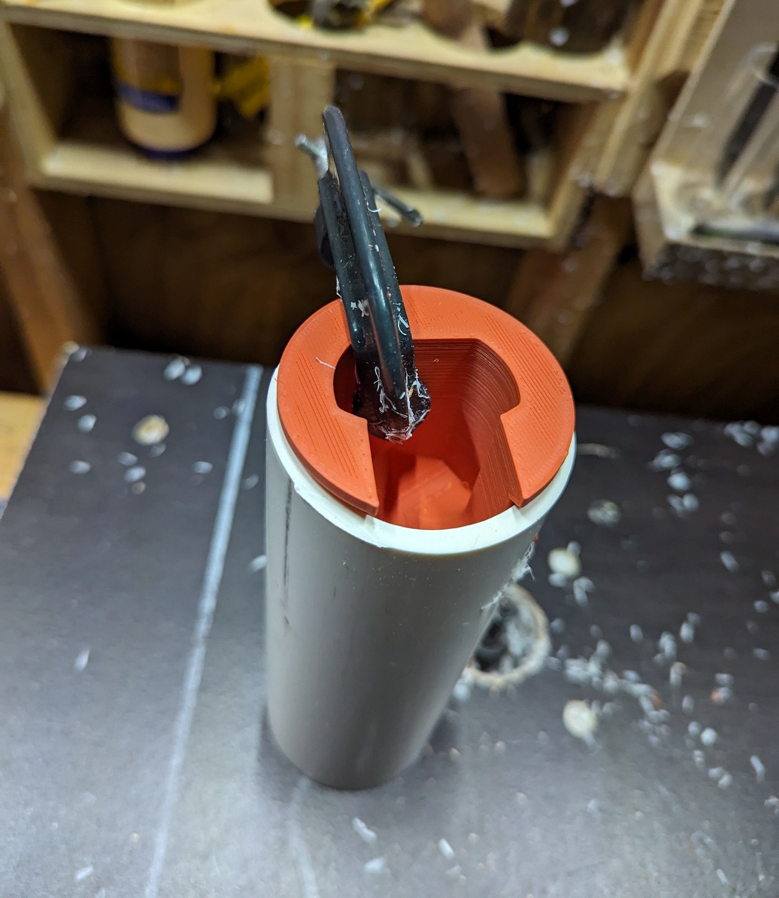
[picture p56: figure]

Figure 17. Router jig inserted into PVC piope and secured with c-clamp.

3. Route the first of three notches in the PCV pipe, going slowly. Make sure that the router bit does not contact the c-clamp.

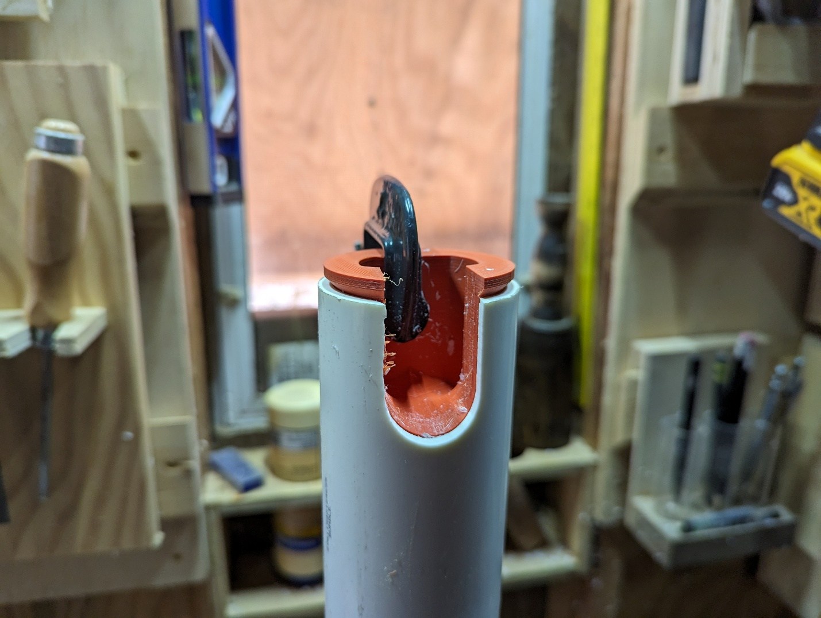
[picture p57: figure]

Figure 18. The first notch routed into the PCV pipe.

4. Clean up your work surface. Remove the first router jig and insert the jig labelled RouterJigForHousing2.3mf int the base of the PVC pipe such that the notch projection slides into the notch that you just routed. Secure with a c-clamp and route the notch, taking care to go slowly and not let the route bit contact the c-clamp.

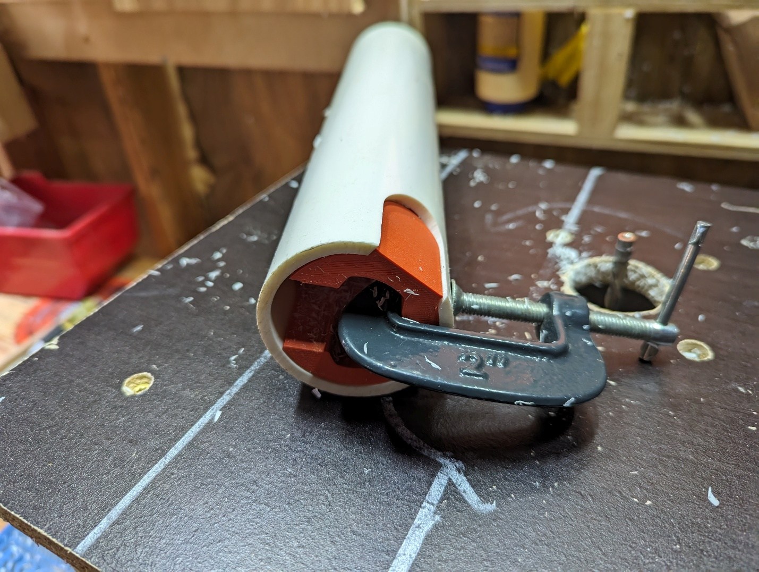
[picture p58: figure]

Figure 19. The second router jig inserted into the PVC pipe and secured with a c-clamp.

5. Route the third notch using the same jig with the notch projection slotted into the second notch. Secure with a c-clamp and route the notch, taking care to go slowly and not let the route bit contact the c-clamp.
6. Remove the jig and clean up your workspace. You should now have an OpenCTD housing with three clean notches routed into the base. With a vacuum or blower, collect any stray pieces of PVC and dispose of safely.
7. Lightly sand the inside bottom of the tube, just above where you cut the slots or
holes. This will provide a good surface for the epoxy to adhere to.

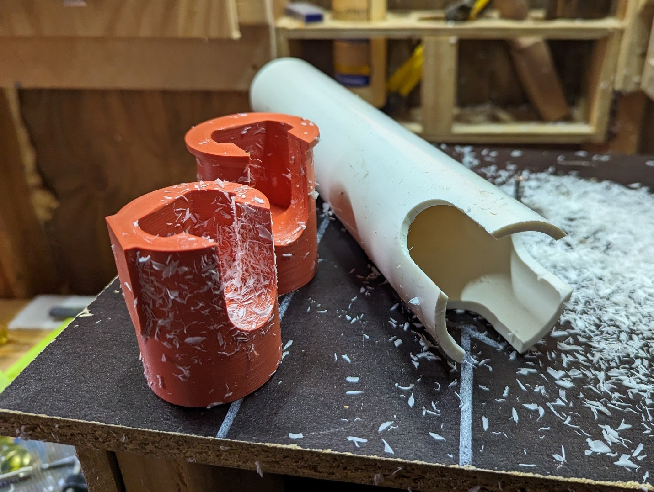
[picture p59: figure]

Figure 20. Completed PVC housing made on a router table.

If you don’t have a router table

If you don’t have access to a router table, you can cut notches using a drill with a 1” bit and a jigsaw or handsaw. It won’t look as pretty, but it will work just fine. Depending on how you intend to use your OpenCTD, you may not need notches at all, or you can simply drill holes in the base to allow water flow without cutting full notches.

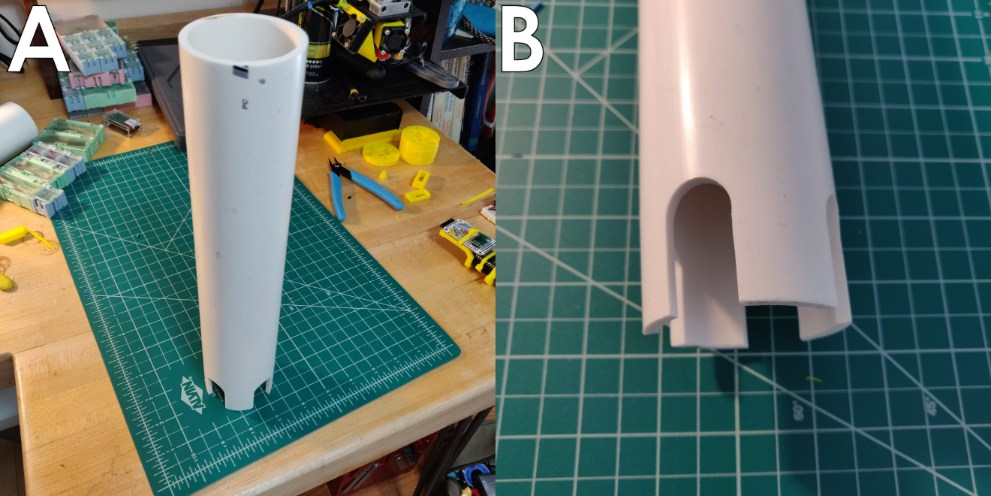
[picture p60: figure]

Figure 21. 12" PVC pipe (A) with notches cut at the base (B).

Though seemingly simple, this set-up has several advantages. Underwater housings are notoriously expensive. Using a PVC pipe instead of a conventional housing with sealed mechanical pass-throughs is the single largest cost-saving step in the entire CTD construction process. This allows us to keep costs down without compromising on sensor quality.
For instruments that are deployed in high-traffic areas long-term, there is also a benefit in having an oceanographic instrument that appears “cheap”. It will be far less likely to be interfered with by curious passersby.

Building the Sensor Package

It’s time to create a waterproof pass through for all of your OpenCTD probes. To build the sensor package, first disconnect the temperature, pressure, and conductivity sensors from the carrier board.

Pot the Pressure Sensor

The 3D printed baseplate provides a template for accurately aligning all five sensors as well as an end-stop to prevent epoxy from leaking out during potting. The pressure sensor sits in the center of the template and fits snuggly into the central hole. This sensor will be potted first with 2-ton instant epoxy to protect the circuits before the full sensor assembly is sealed. Be extremely careful not to get any epoxy on the gel of the pressure sensor.

1. Seat the pressure sensor into the central hole on the side with the large square indentation and ensure that the actual sensor sits flush with the bottom face of the baseplate. Do not apply too much pressure to the sensor housing or the metal ring that contains the gel cap can become detached. If this happens, the sensor cannot be repaired. If the sensor will not seat into the baseplate, use a knife, deburring tool, or other cutting instrument to slightly widen the opening until the sensor seats. Do not force it in, it should be a snug but comfortable fit that will hold in the epoxy applied in step 2.
2. Once the sensor is correctly seated, apply enough instant epoxy to fill the entire central rectangular indentation. The epoxy will settle during pouring as it flows under the circuit board.
3. Carefully check that no epoxy is leaking out through the central hole.

Figure 22: SparkFun MS5803-14BA Pressure Sensor Breakout potted in Epoxy. Topside view on right, underside on left. Note, image from Rev7 OpenCTD, baseplate for Rev8 OpenCTD only has 3 through-holes.

4. Let the assembly sit for a 10 to 20 minutes to allow the epoxy to set.
5. Once the epoxy has set, insert the PT1000 temperature probe into the smaller of the two holes such that 1.5 to 2 cm extends out of the bottom of the baseplate.
6. Insert the conductivity probe into the large hole such that 1.5 to 2 cm extends out of the bottom of the baseplate. If the probe will not seat into the baseplate, use a knife, deburring tool, or other cutting instrument to slightly widen the opening until the sensor seats. It will be a very snug fit.

Pot the OpenCTD

It is time to permanently seal the base of the OpenCTD. Once the epoxy has been mixed and injected, it is essential that you do not move or disturb the housing until the E/A120-HP epoxy cures. Within the first 20 minutes, you may gently lift the housing vertically to check that no epoxy is leaking out the bottom. Do not submerge the OpenCTD until the epoxy has cured for at least 24 hours.

1. Ensure that you can slide the sensor baseplate up into the bottom of the CTD
so that it sits just above the flow-through holes or notches with the sensors protruding out the bottom but protected by the housing. If the fit is too tight, use a deburring tool to knock down the edges of the 3D-printed parts.
2. Push the baseplate into the housing such that the sensors sit slightly back from the rim of the PVC pipe and baseplate clears any notches cut in the sides of the pipe.
3. Reconnect all the sensors to the carrier board and double check that all three probes are still reading.
4. Ensure that the inside of the PVC pipe is clean and free of obstruction.

ENSURE EVERYTHING IS SET CORRECTLY BEFORE PROCEEDING TO THE NEXT STEP.

5. Using the 50mL cartridge gun and venturi mixing nozzle, inject the full 50mL of 2-part epoxy into the OpenCTD housing.
6. Check to ensure that nothing is leaking and let the epoxy cure undisturbed for up to 24 hours. We have generally found that an overnight cure is sufficient for testing at the surface.

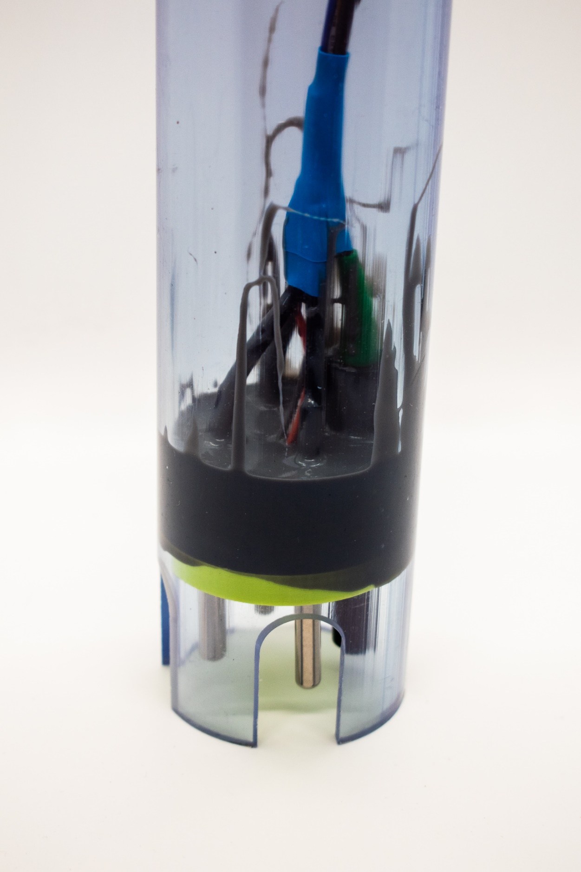
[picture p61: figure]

Figure 23. A clear OpenCTD showing the thick epoxy potting layer.

## Calibration and Data Management

One of the most significant challenges with any open-source science hardware is calibration. Commercial CTDs often require expensive service contracts in order to maintain data quality. The OpenCTD is designed to ensure that the end user is capable of calibrating and maintaining their own equipment, independent of any manufacturer.

While comprehensive validation of the OpenCTD requires access to professionally calibrated instruments maintained in a controlled environment, it is not necessary to do a full validation test for every instrument. This level of validation is for those for whom a high degree of confidence and extreme precision are needed. For environmental monitoring, conservation, ecology, management, and most other use cases, an OpenCTD calibrated against salinity standards and general-purpose temperature sensors is adequate.

As the community grows, validated OpenCTDs can be used to benchmark newly built instruments.

A Microsoft Excel and Google Sheet template is available in the OpenCTD GitHub repository. This template will take raw data from the OpenCTD and make the necessary conversions to create human-readable water column profiles.

Pressure (Depth)

The OpenCTD uses the MS5803 14-bar pressure sensitive chip from Measurement Specialties designed for SCUBA dive watches and depth gauges. This chip contains a pressure sensitive resistor embedded in a gel matrix. The pressure sensor is rated to 140 meters depth. A 30-bar chip, which can double the operating depth of the OpenCTD, is also available, though requires additional customization.

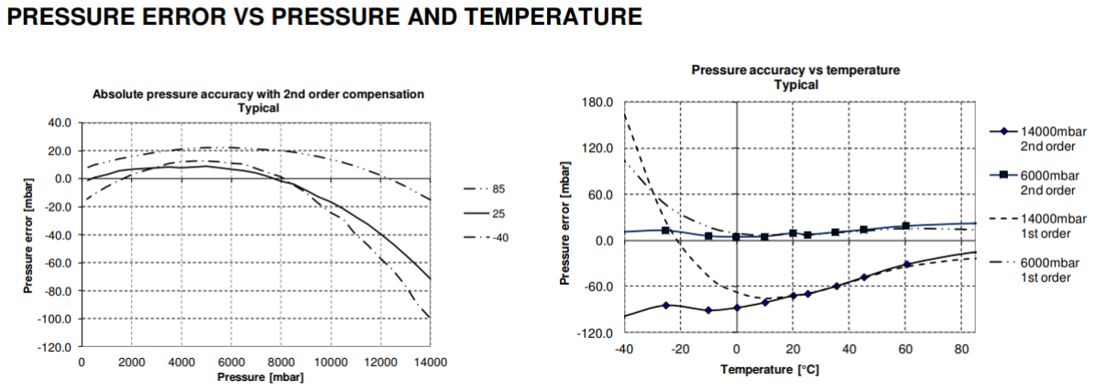
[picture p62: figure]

Figure 24. Pressure sensor error versus ambient pressure and temperature for the MS5803-14BA pressure sensor. Provided by manufacturer.

The MS5803 is a factory-calibrated pressure sensor capable of outputting absolute pressure up to 0.2 millibar resolution. No additional calibration is needed by the user. The pressure sensor outputs absolute pressure. At sea level, the average standard atmospheric pressure is 1013.25 mbar, though local weather and small changes in altitude will affect this baseline. To convert pressure in millibars to depth in meters, use the following equation:

## D = (P(DEPTH) - P(SURFACE) * 100) / (G * 1000)

Where D is depth in meters; P(DEPTH) is the pressure (in millibars) at depth); P(SURFACE) is the pressure at the surface in millibars; and G is acceleration due to gravity, which for most field purposes can be assumed as 9.81 m/s²
(Fofonoff and Millard Jr, 1983). For high-accuracy and high-resolution commercial CTDs, the latitudinal variation in gravity is considered in the pressure-to-depth conversion as these sensors often offer sub-centimeter accuracy.

For extra accuracy, use the absolute pressure at the surface of the water at the time of deployment by taking the last pressure reading before the conductivity probe contacted the water for P(SURFACE). For deployments in alpine lakes and other high-altitude environments, be aware that surface pressure may be significantly less than 1013.25 mbar.

Temperature

The OpenCTD Rev8 uses a platinum PT1000 temperature sensor potted in a stainless-steel cladding. The sensor has an operating range of -50 to 280

oC. It is a Class B temperature sensor designed for industrial use. The advertised accuracy is ±0.3

oC, however, in field trials, we have seen accuracy consistently as low as ±0.1oC.

Thermal time constant is a measurement of how quickly the thermistor responds to changes in ambient temperature. It is expressed as the time it takes for a thermistor to cool to 63.2% of the total difference between a stable high temperature and a stable low temperature. We determined the thermal time constant for these PT1000 temperature sensors at less than 1 second, though it varies depending on the length of exposed stainless steel cladding.

The PT1000 temperature sensor and MAX31865 is self-calibrating based on the resistance between the two positive leads and the internal resistance on the amplifier. Calibration can drift as the instrument ages. We recommend checking temperature calibration at the beginning of each expedition or once per year. When calibration drifts, a linear offset can generally be applied to correct for changes.

Conductivity (Salinity)

The OpenCTD uses a graphite conductivity probe manufactured by Atlas Scientific. Electrical conductivity probes are relatively simple devices consisting of two electrodes of known surface area and known distance from each other. As conductive fluid passes between the two electrodes, they measure the resistance of the liquid. The Atlas probe has a response time of 90% within 1 second, a 343-meter maximum operating depth, and a 1 to 110oC temperature range. The K 1.0 probes can measure conductivity from 5 to 200,000 µS/cm.

Salinity is derived following the formulas outlined by the 1978 Practical Salinity Scale (Lewis, 1980). Temperature and pressure are integral parts of this calculation, and as such it is recommended that the user use this method for determining salinity instead of using the salinity value derived by the Atlas-Scientific conductivity circuit. The accuracy of the calculated salinity value ultimately depends on the accuracy of each individual sensor.

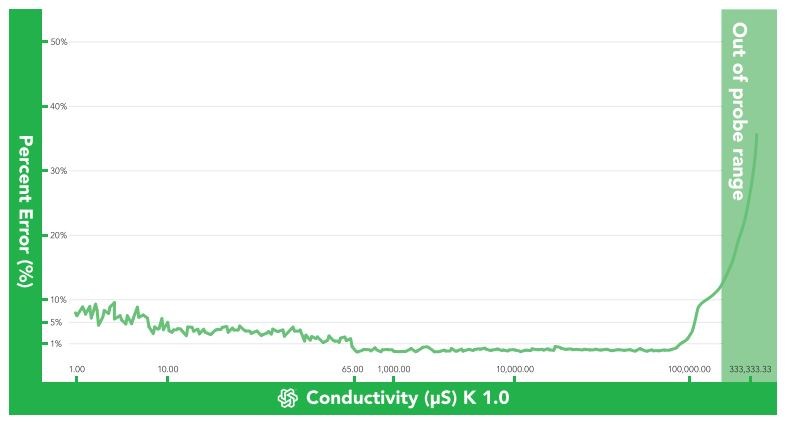
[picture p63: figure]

Figure 25. Accuracy of Atlas Scientific K 1.0 Conductivity Probe and EZO circuit. Data provided by Atlas Scientific.

The conductivity circuit requires a two-point calibration using solutions with a known and precise conductivity. Calibration solutions can be pre-mixed or ordered from a scientific supplier. Atlas Scientific sells a set of calibration standards for their probes. Most calibration standards are designed to be used at 25oC but the Atlas EZO-EC conductivity circuit also allows for temperature compensation if maintaining a stable 25oC temperature is not possible. While any clean glass or plastic container can be used to hold the conductivity solution standards, we recommend a small probe storage bottle to contain the fluid and minimize waste.

Do not return the conductivity solution to the original bottle once it has been used.

In order to clean the conductivity probe and whatever containers you are using to hold the conductivity solution between steps in the calibration process, you will need a source of either distilled water or water filtered through reverse osmosis. Distilled water is readily available in most grocery stores. Reverse osmosis is often used to purify drinking water from seawater and RO machines are often found on oceangoing vessels as well as ground wells. Aquafina brand bottled water is produced using reverse osmosis and has no added minerals, making this brand a cheap source of RO water.

We have developed a simple system for establishing a controlled, thermally stable environment for the calibration process that used the hot bed of a low-cost 3D printer, coupled with a Styrofoam cooler, and a large ceramic thermal mass. A few hours before calibration, set the heated bed of the 3D printer to 25oC.

Find the largest thermal mass available that the OpenCTD housing can fit inside (a heavy coffee mug works well) and place it on the heated bed of the printer. If you cannot maintain a thermostable environment, you can create a cheap isolation chamber by cutting a hole in the bottom of a Styrofoam cooler large enough for the OpenCTD housing to fit snuggly inside. Place the inverted cooler on top of the 3D printer’s heated bed such that the OpenCTD can be inserted through the hole and sit inside the thermal mass.

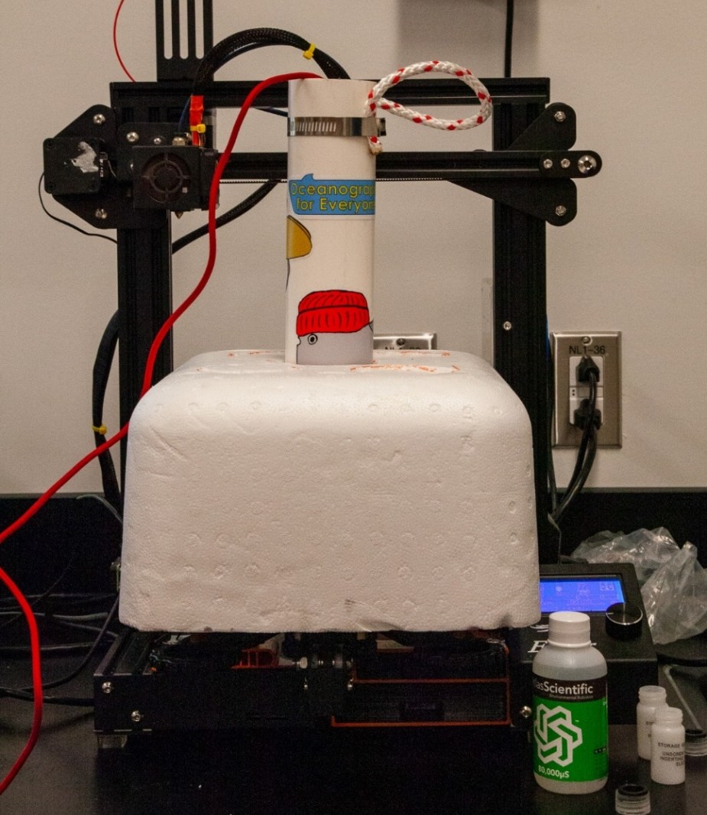
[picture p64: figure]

Figure 26. OpenCTD mounted inside a Styrofoam cooler on top of a 3D printer heat bed in order to maintain an ambient 25oC temperature. Photo by Allie Wilkinson.

When you are ready to calibrate your OpenCTD, insert it into a coffee mug or other thermal mass, and allow it to reach equilibrium.

Two-point calibration is facilitated using Serial_for_EC_Calibration_m0.ino (https://github.com/OceanographyforEveryone/OpenCTD/tree/main/Software/Support/Serial_for_EC_Calibration_m0) (https://github.com/OceanographyforEveryone/OpenCTD/tree/main/Software/Support/Serial_for_EC_Calibration_m0) found in the OpenCTD GitHub repository. If only a single calibration standard is available, one-point calibration is possible, but not recommended. You can monitor the temperature probe through the calibration software.

1. With the control unit powered on and connected to the sensors, upload Serial_for_EC_Calibration_m0.ino to the Adalogger M0. Make sure that the battery is on, as the voltage differential between USB and battery power may affect calibration.
2. Open the serial monitor through the Arduino IDE. Make sure the dropdown menus in the serial monitor are set to “Carriage return” and “9600 baud”. You should see a message with EC Board Info, a note to review this guide, and a reference list of useful commands.
3. Type k,? in the command line and hit enter. This will tell you what the K-value of you probe is set to. It should be set to K=1.0 for most use cases.
a. If the K-value is something other than 1.0 type k,x (where x is the new K-value of the probe) in the command line and hit enter. This is useful if your EZO-EC conductivity circuit reads the incorrect K-value or if you are building an OpenCTD for freshwater deployments using a K 0.1 probe. If there is an error transmitting the command, the serial monitor will report *ER and you should send the command again.
4. To check whether the probe has been previously calibrated type cal,? in the command line and hit enter. If it reads ?CAL,0 the probe has not been calibrated.
5. Type cal,clear and hit enter to clear the previous calibration. It is good practice to send this command even if the circuit reports back that it has not been calibrated. If there is an error transmitting the command, the serial monitor will report *ER and you should send the command again.
6. With the probe dry (be sure there is absolutely no water on the electrodes) enter cal,dry in the command line and hit enter. This will dry calibrate the probe. If there is an error transmitting the command, the serial monitor will report *ER and you should send the command again.

7. Enable continuous monitoring by entering c,1. You will begin to see a steady stream of readings from the conductivity probe updating once per second. If the dry calibration was successful, those values should read 0.00.
8. Clean the probe with distilled or RO water and dry with a clean paper towel. Make sure there is no water trapped in the small hole between electrodes. Clean and dry the container used to hold calibration solution with distilled or RO water and dry with a clean paper towel.
9. Fill the container used to hold calibration solution (we recommend using a beaker or standard ceramic coffee mug) with the less conductive of the two conductivity solutions (12,880 µS if you’re using the Atlas standard solutions). Tap the probe gently to shake out any bubbles.
10. Place the submerged probe in a thermally stable environment. Leave the probe suspended in the calibration solution until readings stabilize (15 minutes is usually sufficient). The reading should be anywhere from 1% to 40% off from the calibration standard. Even once they stabilize, there will be small fluctuations in value. If you leave the probe in for too long, it will ionize the water and the conductivity readings will begin to creep up. A gentle shake will return the solution to its baseline.
11. Type cal,low,y (where y is the known value of the standard. If you are using the Atlas conductivity standard, type cal,low,12880) in the command line and hit enter. The conductivity readings in the serial monitor will not update.
12. Remove the probe from the solution, clean the probe with distilled or RO water, and dry with a clean paper towel. Make sure there is no water trapped in the small hole between electrodes.
13. Fill the container used to hold calibration solution with the more conductive of the two conductivity solutions (80,000 µS if you’re using the Atlas standard solutions). Tap the probe gently to shake out any bubbles.
14. Place the submerged probe in a thermally stable environment. Leave the probe suspended in the calibration solution until readings stabilize (15 minutes is usually sufficient). The reading should be anywhere from 1% to 40% off from the calibration standard. Even once they stabilize, there will be small fluctuations in value. If you leave the probe in for too long, it will ionize the water and the conductivity readings will begin to creep up. A gentle shake will return the solution to its baseline.

15. Type cal,high,y (where y is the known value of the standard. If you are using the Atlas conductivity standard, type cal,high,80000) in the command line and hit enter. The conductivity readings in the serial monitor will update and should read very close to 80,000.

Alternative: For 1-point calibration, suspend the probe in known calibration solution. Leave the probe suspended in the solution until readings stabilize. Enter cal,one,y (where y is the known value of the standard) in the command line and hit enter. Only do
this if you do not have two calibration standards.
16. After calibration is complete, upload the OpenCTD software to the Adalogger
M0.

If you do not have access to a system that allows you to maintain a temperature at a stable 25oC, there are two alternatives for calibration. You can use the temperature compensation feature of the Atlas EZO-EC conductivity circuit to set a different stable temperature for calibration, provided that the environment around the probe is stable at that temperature. You can derive the compensation temperature from the OpenCTDs temperature probes, rounded up to the nearest tenth of a

oC. Set the compensation temperature on the EZO-EC by sending the command t,x through the serial monitor, where x is the compensation temperature rounded to the nearest tenth of a oC. Once temperature compensation is entered, continue through the above two-point calibration protocol. Temperature compensation will reset to 25oC whenever the unit is powered down.

Review the Atlas EZO-EC Datasheet (https://atlas-scientific.com/files/EC_EZO_Datasheet.pdf) for more thorough instructions.

If you cannot maintain a consistent thermal environment, there is one potential alternative that will result in a rough calibration of the probe acceptable for education or for applications where precise salinity measurements are not essential. On the side of bottles of salinity standards provided by Atlas Scientific and others, there is usually a table of compensation values in intervals of 5oC. You can calibrate to the value closest to ambient temperature. This method should only be used if no other alternatives are available.

Conductivity should not need to be calibrated again once the calibration protocol is complete, however it is practice to check calibration at least once per year or whenever components are changed. For more detailed explanation of the calibration process and for an explanation of

Figure 27. Location of conductivity temperature
offsets. Image from Atlas Scientific.

temperature compensation, refer to the Atlas EZO-EC Datasheet (https://atlas-scientific.com/files/EC_EZO_Datasheet.pdf). (https://atlas-scientific.com/files/EC_EZO_Datasheet.pdf)

Each control unit is calibrated to a specific sensor package. Control units are not interchangeable between OpenCTDs without recalibration.

Data Management

The OpenCTD outputs data as a comma delimited text file which can be read by any standard spreadsheet program. It outputs the date and time followed by the pressure sensor in mbar, each individual temperature sensor in oC, and the conductivity sensor in microSiemens. In order to convert those values into human-readable oceanographic data, we have produced an Excel template that takes the raw data and outputs depth in meters, average temperature, and practical salinity units and generates a basic water column profile.

The template will also average readings in batches of 60 to simplify data presentation. It has fields for calibration constants so that users can input the absolute pressure at sea level at the time of deployment and the temperature offset of the OpenCTD temperature probes determined experimentally during the calibration phase.

Although the SD card reader is built into the Adalogger, Arduino M0 microcontrollers do not provide data passthrough, which means the SD card cannot be read directly from the Adalogger. Data is accessed post-deployment by removing the SD card from the Control Unit and connecting it directly to a computer.

Importing into Excel: Open the Excel or Google Sheets template and navigate to the Data Input sheet in the lower left corner. You can copy-paste the desired data points directly into the sheet. If you use the Get Data function, Excel will create a new sheet for the data.

Data clean-up: Depending on when you started and stopped the OpenCTD, you may have dozens to thousands of rows of data from the surface that you don’t need. Using the reading from the pressure sensor and conductivity probe, remove any date that appears to be from the surface (pressure readings around 1010 and conductivity readings at or near 0).

Water column profile: Select the data that you want to analyze and copy/paste it into the “Paste RAW data from OpenCTD” columns on the Calculations sheet. The water column profile graph should update but you will have to edit the source data fields in order to cover all of your data. You can save the water column profile as an image to embed in presentations or download the cleaned and processed data for more analysis. For long deployments, the final column included the data averaged in 1-minute intervals.

## Final Preparation and First Deployment

Precisely how much weight a CTD needs for ballast and how it should be mounted to an instrument or line is entirely dependent on your specific needs. A CTD deployed in a brackish estuary to a relatively shallow depth can sink with no additional weights on something as simple as a handline. A CTD deployed to ocean depths in high current may need to be attached to a weighted anchor line with heavy-duty hose clamps.

Below, we provide a few possible mounting options for the OpenCTD. We recommend for most cases, using the casting loop and a medium-duty Polypro line.

Casting Loop

This is a basic, durable loop for clipping to a handline that can be constructed using a short length of Polypro rope and a 2” hose clamp, as picture below. For extra security and to avoid snags, we recommend that you also wrap the hose clamp in electrical tape.

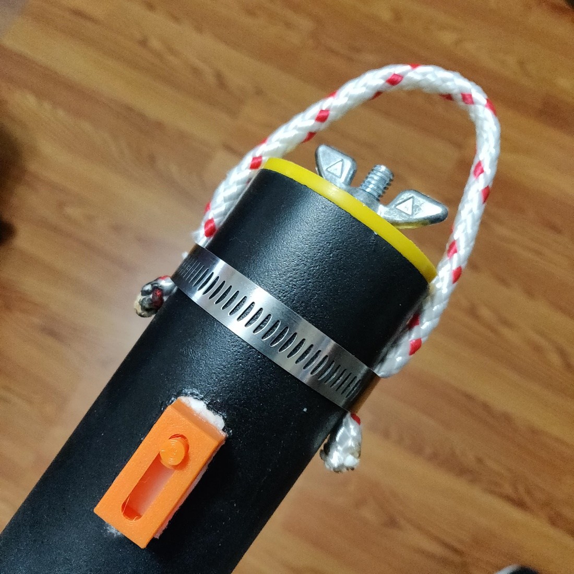
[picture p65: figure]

Figure 28. Finished OpenCTD with optional casting loop.

The potted and sealed OpenCTD is positively buoyant. In order to make the CTD sink, you will need to ballast it with weights. For coastal areas, we have found that 4 to 6-ounces is sufficient to make the OpenCTD slightly negatively buoyant, but the total amount of weight necessary will vary depending on salinity and water conditions. We recommend installing a second casting loop at the bottom of the OpenCTD housing from which you can connect weights below the device.

Weighted Casting Line

For deeper deployments, or operations in high current, a weighted anchor line, with the anchor or weight held several feet below the CTD, with provide substantial negative buoyancy while keeping the unit horizontal. We recommend at least two hose clamps to ensure that the unit stays in position.

Figure 29. Example of OpenCTD attached to weighted anchor line using hose clamps.

Internal Ballast

The OpenCTD is positively buoyant in salt water. As a baseline, we recommend six ounces of standard fishing weights stored inside the housing. This will make the unit slightly negatively buoyant and able to sink in calm waters.

To avoid damaging the electronics, it is best practice to remove the weights between deployments so that they don’t shake around during transportation. Wrapping them in rubber or electrical tape will also minimize movement.

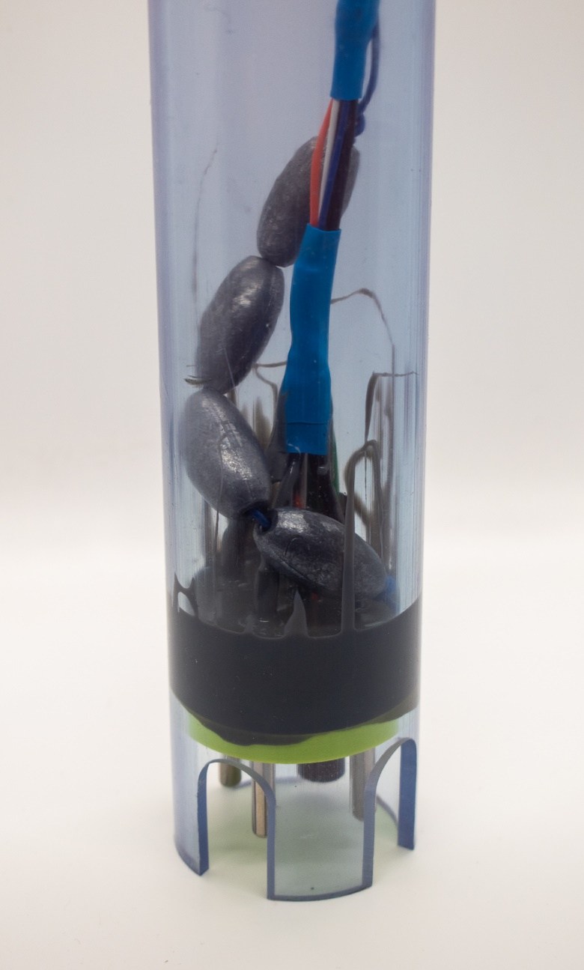
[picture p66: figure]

Figure 30. Clear OpenCTD with fishing weights inside.

External Ballast

There are an infinite number of ways to affix weights to the outside of the OpenCTD. We’ve seen everything from lead flashing wrapped around the housing to small gym weights hung underneath. We recommend avoiding having external weights attached directly to the CTD. It is preferable to mount the entire OpenCTD to a heavier object for deployment. This is a great opportunity to encourage your students to get creative.

The First Deployment

It is finally time to make your first cast! If you have an OpenCTD Rev8 Kit or bought stickers from the Oceanography for Everyone store, affix you stickers now.

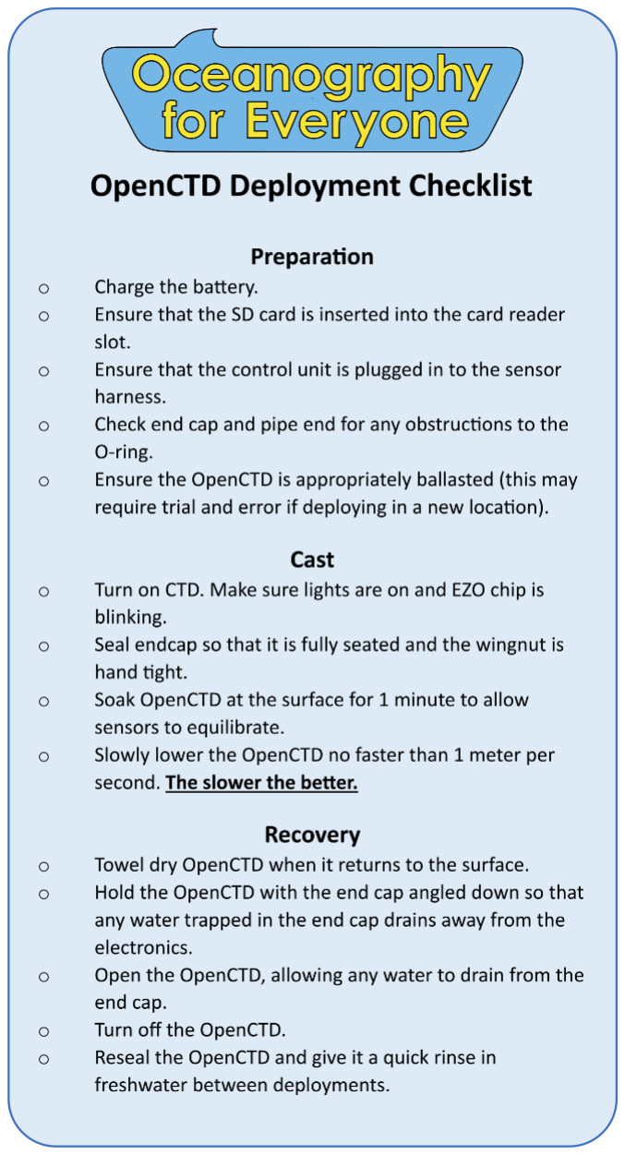
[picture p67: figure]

Figure 31. OpenCTD deployment sticker with a checklist of task to complete before, during, and after each cast.

The OpenCTD is sealed with a 2” plumbers test cap, tightened with a large wingnut. The wingnut should be hand tight. We have provide a 3D-printed wrench to aid in tightening the test cap to the appropriate level.

The OpenCTD’s maximum operating depth was established both through field trials and tests in a pressure chamber. The maximum operating depth of the sensor system is 140 meters; however, the housing has only been tested consistently to 100 meters depth without leaks or catastrophic failure. Because each OpenCTD will be slightly different, using the 100-meter benchmark provides a good margin of error for operation. Before the first data cast, test your CTD by submerging just the housing without the control unit to the desired depth and confirm that the unit did not flood before deploying with the battery and control unit.

If the CTD housing does flood, immediately flush the interior and JST connector with distilled water and dry thoroughly. As long as there is no corrosion on the connector and it is dry when under load, there should be no damage to the electronics.

A brand new OpenCTD will be positively buoyant. Additional weight can be added into the housing or attached to the outside. Lead shot or fishing weights are particularly useful for this. If you are doing a line cast, you will need to secure the CTD to a sturdy line using hose clamps, waterproof tape, or other adhesive solutions. You will want to experiment with different weights to find the ideal ballast for the conditions that you will be deploying in.

Check that the inside surface of the PVC pipe is clean and free of debris. To ensure no leaks, the test cap used to seal the unit should be fully seated with no obstructions between the pipe wall and the rubber gasket and be hand tight. Seat the test cap onto the housing and tighten the wingnut. The wingnut should be as tight as possible without tool assistance and the cap should not move or turn. Over time, salt may build up on the wingnut, causing the crew to bind. WD-40 or other water displacing lubricants can help loosen up the screw.

Your OpenCTD is now ready to take the plunge! Gently lower into the water and descend no more than 1 meter per second. The slower the better. For the first cast, and especially if it has sat unused for a while, descend to 5 meters without the control unit, hold for several minutes, then recover and check that no leakage has occurred. Once it passes the first soak test, you're ready to insert the control unit and collect ocean data.

While calibration plays a significant role in affecting data quality, response times and the method of deployment also have an influence. The conductivity sensor maintains a response time of approximately one second for a 90% value (Atlas-Scientific, 2017). The pressure sensor response time is variable between 0.5 to 8.22 m/s depending on the resolution selected by the user (Measurement Specialties, 2012). In order to ensure that the device has reached relative equilibrium with the surrounding water, it is necessary to leave it at station for several minutes before beginning an in-situ deployment. When faster response time is required, the sensors used in the most recent version of the OpenCTD can easily be replaced by more accurate, but also more expensive alternatives.

While handling the OpenCTD, take care not to damage the sensors, especially the gel pack around the pressure sensor. Sand can be particularly destructive to the gel back and can become lodged inside the through hole on the conductivity probe. When working from a beach, take extra care to avoid allowing the sensors to come in contact with the sand.

Stewardship

Whenever you introduce a new tool into the marine environment, you run the risk of introducing additional harm to the ecosystem. Though OpenCTDs can serve as a valuable tool for ocean conservation, they also have the potential to negatively impact marine animals and ecosystems. We have developed a set of guidelines for minimizing potential negative impact when introducing new technologies into marine ecosystems (Thaler et al., 2019, 2015). Though these guidelines specifically address small underwater robots, they are equally applicable to OpenCTDs and other instrumentation platforms.

We ask that you read the following two short papers and approach your project with a stewardship ethic and an eye towards ensuring that your work will not contribute additional harm to the ecosystems that you are working in.

- Robots as Vectors for Marine Invasions: Best Practices for Minimizing Transmission of Invasive Species Via Observation-Class ROVs (https://journals.sagepub.com/doi/full/10.1177/194008291500800308)
- Bot Meets Whale: Best Practices for Mitigating Negative Interactions Between Marine Mammals and MicroROVs
(https://www.frontiersin.org/articles/10.3389/fmars.2019.00506/full)

## Works Cited

Fofonoff, N.P., Millard Jr, R.C., 1983. Algorithms for the computation of fundamental properties of seawater. UNESCO Technical Papers in Marine Sciences 44. https://doi.org/10.25607/OBP-1450
Hooker, S.K., Boyd, I.L., 2003. Salinity sensors on seals: use of marine predators to carry CTD data loggers. Deep Sea Research Part I: Oceanographic Research Papers 50, 927–939. https://doi.org/10.1016/S0967-0637(03)00055-4
Lewis, E., 1980. The practical salinity scale 1978 and its antecedents. IEEE Journal of Oceanic Engineering 5, 3–8. https://doi.org/10.1109/JOE.1980.1145448
Oskui, S.M., Diamante, G., Liao, C., Shi, W., Gan, J., Schlenk, D., Grover, W.H., 2016. Assessing and Reducing the Toxicity of 3D-Printed Parts. Environ. Sci. Technol. Lett. 3, 1–6. https://doi.org/10.1021/acs.estlett.5b00249
Stammer, D., Balmaseda, M., Heimbach, P., Köhl, A., Weaver, A., 2016. Ocean Data Assimilation in Support of Climate Applications: Status and Perspectives. Annual Review of Marine Science 8, 491–518. https://doi.org/10.1146/annurev-marine-122414-034113
Stephen, R.C., Howard, F.J., Dean, R., Susan, W., Ariel, T., Mathieu, B., Denis, G., Jianping, X., Sylvie, P., Thresher, A., Traon Pierre-Yves, L., Guillaume, M., Birgit, K., Kjell-Arne, M., Velez-Belch Pedro, J., Isabelle, A., Brian, K., Jon, T., Molly, B., Steven, J.R., 2016. Fifteen years of ocean observations with the global Argo array. Nature Climate Change Marine Res Inst 6. https://doi.org/10.1038/NCLIMATE2872
Sverdrup, H.U., Johnson, M.W., Fleming, R.H., 1942. The Oceans: Their Physics, Chemistry, and General Biology. Asia Publishing House.
Thaler, A., Parsons, E.C.M., de Vos, A., Rose, N.A., Smith, C., Fretz, D., 2019. Bot Meets Whale: Best Practices for Mitigating Negative Interactions Between Marine Mammals and MicroROVs. Front. Mar. Sci. 6. https://doi.org/10.3389/fmars.2019.00506 Thaler, A., Sturdivant, S.K., Neches, R.Y., Levenson, J.J., 2024. The OpenCTD: A Low-Cost, Open-Source CTD for Collecting Baseline Oceanographic Data in Coastal Waters. Oceanography 37, 167–173. https://doi.org/10.5670/oceanog.2024.602
Thaler, A.D., Freitag, A., Bergman, E., Fretz, D., Saleu, W., 2015. Robots as vectors for marine invasions: Best practices for minimizing transmission of invasive species via observation-class ROVs. Tropical Conservation Science 8.
Thomson, R.E., Emery, W.J., 2014. Data Analysis Methods in Physical Oceanography. Newnes.

## Resources and Datasheets

General Guides

Soldering is Easy: Here’s How To Do It: mightyohm.com/files/soldercomic/FullSolderComic_EN.pdf

Environmental Monitoring with Arduino: Building Simple Devices to Collect Data About the World Around Us: https://amzn.to/2M17yUi

Sensors

MS5803-14BA Miniature 14 bar Module: https://cdn.sparkfun.com/datasheets/Sensors/Weather/ms5803_14ba.pdf

EZO-EC Conductivity Circuit Datasheet – https://www.atlas-scientific.com/_files/_datasheets/_circuit/EC_EZO_Datasheet.pdf (https://www.atlas-scientific.com/_files/_datasheets/_circuit/EC_EZO_Datasheet.pdf)

EC K 1.0 Conductivity Probe Datasheet – https://www.atlas-scientific.com/_files/_datasheets/_probe/EC_K_1.0_probe.pdf (https://www.atlas-scientific.com/_files/_datasheets/_probe/EC_K_1.0_probe.pdf)

How to properly cut your probe cable – https://files.atlas-scientific.com/how-to-properly-cut-probe-cables.pdf

Conductivity Accuracy Graph – https://www.atlas-scientific.com/_files/instructions/conductivity_accuracy_graph.pdf (https://www.atlas-scientific.com/_files/instructions/conductivity_accuracy_graph.pdf)

## Bill of Materials

While we strive to maintain an up-to-date Bill of Materials with the best available prices, local availability and price fluctuations mean that this will never reflect the best prices for every component. Parts that are only available in bulk may be difficult to source individually. Always check alternative suppliers for better prices. The leftmost column corresponds to where each part appears in the checklist and, subsequently, the build order.

Item | Links | Price | Price per CTD
| Adafruit Feather M0 Adalogger | https://www.adafruit.com/product/2796https://amzn.to/36DrCm4https://www.digikey.com/en/products/detail/adafruit-industries-llc/2796/5804105 (https://www.digikey.com/en/products/detail/adafruit-industries-llc/2796/5804105) | $19.95 | $19.95
| Pack of 2 Micro SD Card 4GB Flash Memory Card Micro SDHC with SD Adapter (4 GB) | https://amzn.to/4gfQVAU Check local electronics stores and online vendors | $15.49 | $7.75
| MicroUSB Cable | https://amzn.to/3CEElp0 Check local electronics stores and online vendors | $5.24 | $2.62

Prepare the Adalogger M0

Item | Links | Price | Price per CTD
OpenCTD Rev8 Custom Carrier Board | Available from Oceanography for Everyone https://oceanographyforeveryone.bigcartel.com/ | $15.00 | $15.00
Pin Header, Male and Female Single Row Header Pins | https://amzn.to/3Sqe4Xo Check local electronics stores and online vendors | $7.49 | $1.12
Breadboard-friendly SPDT Slide Switch | https://www.adafruit.com/product/805 Check local electronics stores and online vendors | $0.95 | $0.95
10 kΩ Resistor (2) | https://amzn.to/3JcUFjk Check local electronics stores and online vendors | $7.85 | $0.16
JST PH 2mm 4-pin Vertical Connector | https://www.adafruit.com/product/4390 Check local electronics stores and online suppliers | $3.50 | $0.35

Prepare the Carrier Board

Item | Links | Price | Price per CTD
| Adafruit DS3231 Precision RTC | https://www.adafruit.com/product/5188 | $13.95 | $13.95
| CR1220 3V Coin Cell Battery | https://www.adafruit.com/product/380https://amzn.to/2NYFQpf Check local electronics stores and online suppliers | $0.95 | $0.95

Prepare the Real-Time Clock

Item | Links | Price | Price per CTD
| MAX31865 PT1000 Temperature Amplifier | https://www.adafruit.com/product/3648 | $14.95 | $14.95
| 3-pin JST SM Plug + Receptacle | https://www.adafruit.com/product/1663 | $1.50 | $1.50

Prepare the MAX31865 PT1000

Temperature Amplifier

Item | Links | Price | Price per CTD
| Black Nylon Machine Screw and Stand-off Set – M3 Thread | https://www.adafruit.com/product/4685 Check local electronics stores and online suppliers | $16.95 | $0.36
| Mini Conductivity K 1.0 Kit | https://atlas-scientific.com/kits/mini-conductivity-k-1-0-kit/ (https://atlas-scientific.com/kits/mini-conductivity-k-1-0-kit/) | $199.99 | $199.99

Assemble the Control Unit

Item | Links | Price | Price per CTD
| Lithium Ion Polymer Battery Ideal For Feathers - 3.7V 400mAh | https://www.adafruit.com/product/3898 | $6.95 | $6.95
Powering the
OpenCTD
Item | Links | Price | Price per CTD
| Platinum RTD Sensor - PT1000 | https://www.adafruit.com/product/3984 | $14.95 | $14.95
| Solder Seal Wire Connectors, Waterproof Heat Shrink Butt Connectors Terminals | https://amzn.to/4vfpDPU Check local electronics stores and online suppliers | $26.99 | $0.47

Prepare the PT1000
Temperature Probe

Item | Links | Price | Price per CTD
| SparkFun Pressure Sensor Breakout -MS5803-14BA | https://www.sparkfun.com/sparkfun-pressure-sensor-breakout-ms5803-14ba.html (https://www.sparkfun.com/sparkfun-pressure-sensor-breakout-ms5803-14ba.html) | $80.50 | $80.50
| 22 Gauge Silicone Wire Kit 10 Color Each 5 ft Flexible 22 AWG Stranded Tinned Copper Wire | https://amzn.to/4aOldae Check local electronics stores and online suppliers | $11.48 | $0.92
| JST Plug Connectors | https://amzn.to/4vi6MUq Check local electronics stores and online suppliers | $7.39 | $0.18

Prepare the Sparkfun
Pressure Sensor
Item | Links | Price | Price per CTD
| 2" PVC Pipe 1FT Long Sch40 | https://amzn.to/4orlhCy Check local hardware stores and online suppliers | $15.99 | $8.00
Cutting the

PVC Housing

Item | Links | Price | Price per CTD
| Loctite Epoxy Five Minute Instant Mix | https://amzn.to/3tuKM8q Check local hardware stores and online suppliers | $14.49 | $7.25
Pot the Pressure

Sensor

Item | Links | Price | Price per CTD
| Epoxy, Loctite E-120hp, 1.69 FL. oz. Cartridge 6430A24 | https://www.mcmaster.com/products/6430a24/ | $24.13 | $24.13
| Long Taper Tip Nozzle with Bayonet Connection for Two-Part Cartridge | https://www.mcmaster.com/74695A12/ | $2.57 | $0.13

Potting the
OpenCTD
Item | Links | Price | Price per CTD
| Hose clamp (AB-36/46mm to 70mm) | https://amzn.to/3t7G1UX Check local hardware stores and online suppliers | $14.99 | $6.00
| 1/4” PolyPro Rope | https://amzn.to/3w7su1G Check local hardware stores and online suppliers | $7.80 | $0.32
| Oatey Gripper 2” Mechanical Test Plug | https://www.lowes.com/pd/Oatey-2-in-Gripper-PVC-DWV-Test-Plug/3880607 (https://www.lowes.com/pd/Oatey-2-in-Gripper-PVC-DWV-Test-Plug/3880607) Check local hardware stores and online suppliers | $8.18 | $8.18

Final Preparation and
First Deployment
Item | Links | Price | Price per CTD
| Conductivity Calibration K 1.0 Set | https://atlas-scientific.com/calibration-solutions/conductivity-calibration-k-1-0-set/ (https://atlas-scientific.com/calibration-solutions/conductivity-calibration-k-1-0-set/) | $15.99 | $15.99
Calibration

Alternate Pressure Sensor

Item | Links | Price | Price per CTD
MS5803-14BA Pressure Sensor SMC | https://www.digikey.com/en/products/detail/te-connectivity-measurement-specialties/MS580314BA01-00/5277631 (https://www.digikey.com/en/products/detail/te-connectivity-measurement-specialties/MS580314BA01-00/5277631) | $23.10 | $23.10
OpenCTD Custom Pressure Sensor Breakout Board | Available from Oceanography for Everyone | $10.00 | $10.00
10 kΩ Resistor | https://amzn.to/3JcUFjk Can be sourced from any electronics supplier | $6.18 | $0.06
0.1 uF Capacitor | https://amzn.to/32tMBol Can be sourced from any electronics supplier | $5.92 | $0.24

Alternate Pressure Sensor

## Appendix A. Alternate Pressure Sensor

Components for Oceanography for Everyone Pressure Sensor Breakout Board

MS5803-14BA Pressure Sensor SMC | OpenCTD Pressure Sensor Breakout Board
10 kOhm Resistor | 0.1 uF Capacitor

DIY Pressure Sensor

To build the pressure sensor, you will need to surface mount the pressure sensor chip onto the OpenCTD Pressure Sensor Breakout Board. This is the most challenging soldering step in the entire build and requires a steady hand. The pressure chip is able to withstand high heat for a short amount of time, as long as there is no direct contact. Be extremely careful not to touch the gel covering the pressure sensor.

1. Add a small amount of solder to each pad. If you have solder flux, add a dab of flux to each pad to help the solder flow.
2. Ensure that the dot and notch on the pressure sensor line up with the dot on the OpenCTD Pressure Sensor Breakout Board. Solder the sensor in place by applying a small amount of solder to the vertical grooves and drawing it down onto the solder pads. Be careful not to short any connections.
3. On the side opposite the pressure chip, solder a 10 kOhm pull-up resistor to the pins labeled 10 kOhm.
4. On the side opposite the pressure chip, solder a 0.1µF capacitor to the pins labeled 0.1µF.
5. On the side opposite the pressure chip solder a 20 cm length of wire to the pins labeled CLK, GND, SDA, and VCC. Keep track of which wire goes to which pin by color-coding each pin (we recommend red for VCC; black for ground; yellow for CLK; and blue for SDA).
6. Strip 1/4 cm of insulation from the exposed ends of each wire.

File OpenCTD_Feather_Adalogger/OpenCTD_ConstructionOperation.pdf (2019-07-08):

OpenCTD - 1

# OpenCTD

# Construction and Operation

Andrew Thaler
Kersey Sturdivant
Russell Neches
Ian Black

## Contents

1.0 Overview | 4
1.1 Skills Needed | 5
1.2 Project Status | 6
1.3 Field Trials | 6
2.0 Materials and Preparation | 8
2.1 Bill of Materials | 8
2.2 Recommended Components | 9
2.3 Tools and Consumables | 10
2.4 3D-Printing | 11
2.5 Preparing the Adalogger and RTC | 13
2.6 Software and Libraries | 14
2.6.2 Required Arduino Libraries | 15
2.7 Preparing the housing | 16
Benchmark 1: Confirm Software Install and Adalogger/RTC assembly | 17
3.0 Sensor Assembly and Breadboard Testing | 18
3.1 Pressure Sensor | 18
3.2 Temperature Sensors | 19
3.3 Conductivity Sensor | 21
Benchmark 2: Breadboarding the Circuit | 22
Breadboard Diagram | 24
4.0 Assembling the Main Control Unit | 25
4.1 Preparation | 25
4.2 Soldering the RTC | 26
4.3 Populating the Perma-Protoboard | 27
Benchmark 3 – Testing the Master Control Unit | 30
5.0 Mounting and Potting Sensors | 31
5.1 Baseplate and Potting the Pressure Sensor | 31
5.2 Creating the Connector | 33
5.3 Battery and Switch | 35
5.3 Potting the OpenCTD | 37
6.0 Calibration and Data Management | 39

6.1 Pressure (Depth) | 39
6.2 Temperature | 40
6.3 Conductivity (Salinity) | 41
6.4 Data Management | 43
7.0 The First Deployment | 44
8.0 Works Cited | 46
9.0 Resources | 47

## 1.0 Overview

The ocean is not uniform, it its filled with swirling eddies, temperature boundaries, layers of high and low salinity, changing densities, and other physical characteristics invisible to surface observers (Sverdrup et al., 1942). By measuring salinity, temperature, and depth, scientists can unlock ocean patterns hidden beneath the sea's surface. To reveal these patterns, oceanographers use a CTD—an instrument that measures Conductivity (which serves as a proxy for salinity), Temperature, and absolute pressure (used to determine water Depth; Thomson and Emery, 2014).
CTDs come in a variety of shapes, sizes, and applications. Most oceanographic vessels have a CTD connected to a rosette system, which can house other instruments and collect physical water samples in parallel with real-time data collection. CTDs are also commonly attached to moorings, autonomous underwater vehicles (AUVs), remote-operated vehicles (ROVs), and, on occasion, marine animals (Hooker and Boyd, 2003).

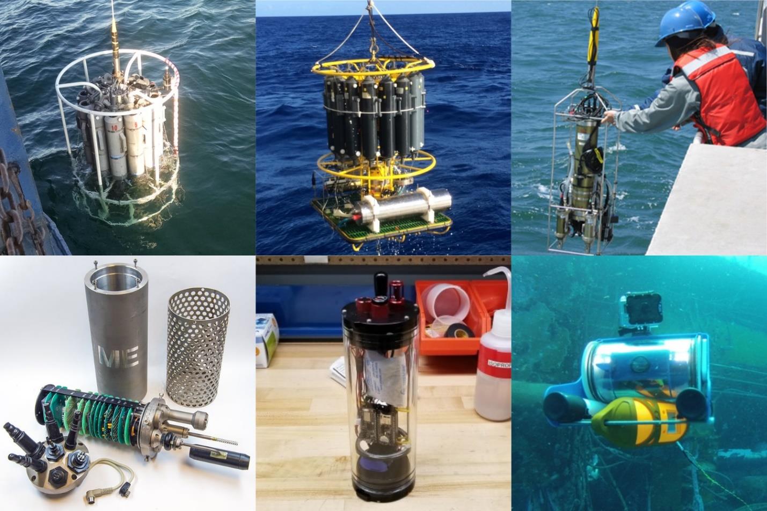
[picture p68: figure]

Figure 1. A selection of various CTDs used for field work. Top left: A CTD and rosette deployed from a NOAA boat (WHOI); top center: A CTD and rosette deployed by IFREMER; top right: a student deploys a CTD (MIT); bottom left: an 80s era ME GRISARD CTD; bottom center: the CTDizzle open-source CTD by Ian Black; bottom right: a YSI Castaway affixed to an OpenROV 2.3 (Sofar).

Commercial CTDs are expensive, with the most affordable models costing as much as $6,000.00. For near-shore oceanographic research on the continental shelf, where the water depth rarely exceeds 200 meters, this can be a prohibitive cost. The expense of the CTD is a barrier-to-entry for formal and informal researchers working with limited budgets, including scientists from developing nations, citizen oceanographers, environmental educators, and students of all levels interested in understanding their local coasts and waterways.
Climate change, ocean acidification, and sea level rise have created an urgent need for extensive measurements of oceanographic conditions both globally and locally (Stammer et al., 2016; Stephen et al., 2016). At the same time, government funding at both state and federal levels for climate change research can be unreliable, if not wholly non-existent. This creates a pressing need for low-cost alternatives to common scientific instruments that allow formal researchers to stretch the impact of extant funding awards while simultaneously allowing informal researchers (such as environmental monitoring organizations and non-governmental organizations, as well as concerned community members) to contribute water-quality measurements. The OpenCTD can help fill that need.
The OpenCTD is a low-cost, open-source CTD designed intentionally for citizen scientists, educators, and researchers working in nearshore coastal ecosystems, where entire research projects can be conducted for less than the cost of a commercial CTD. It was developed by a core team of marine ecologists in collaboration with a distributed community of scientists, engineers, makers, and conservation practitioners. It is assembled from components commonly available at large hardware stores or through major online retailers. An Arduino-based microcontroller controls a battery of sensors sealed within a PVC pipe. Power is provided by a standard 3.7V lithium polymer battery and data is stored as a tab-delimited text-file accessed via SD card.
The OpenCTD is designed to be built by the end-user, providing both access to the tools of oceanography and the skills to maintain, repair, and replace OpenCTDs. For educators looking a for novel, in-depth, hands-on STEM experience for advanced students, the process of building an OpenCTD can offer a great introduction to coding, 3D-printing, hardware prototyping, and electronics. Construction of an OpenCTD can provide a practical foundation for courses in oceanography, environmental science, or physics.
As you build your OpenCTD please reach out to the team at Oceanography for Everyone if you have any questions or feedback about the process. We love to keep up with the community of people constructing and using these devices. During assembly and while using an OpenCTD or other Oceanography for Everyone tools, please consider tweeting or Instagramming using the hashtag #HackTheOcean so that the community can follow your efforts.

1.1 Skills Needed

To construct an OpenCTD, you will need to be familiar with basic soldering and coding, but this project can serve as a fantastic introduction. We have designed this guide to be approachable to people learning these skills. With a few hours of practice, you can develop the soldering skills necessary to build an OpenCTD.
For absolute beginners, we recommend working through Soldering is Easy: Here’s How To Do It by Mitch Altman, Andie Nordgren, and Jeff Keyzer, which is an accessible and approachable introduction to soldering fundamentals.

- Soldering is Easy: Here’s How To Do It: mightyohm.com/files/soldercomic/FullSolderComic_EN.pdf

We have had great success using the MightyOhm Geiger Counter Kit and the Mega Menorah 9000 Soldering Kit to teach soldering and basic electronic principles to students from ages 7 to 70. However, preparing the components needed for an OpenCTD will provide most students with sufficient grounding to tackle the more complex elements of constructing an OpenCTD.

- Geiger Counter Kit - Radiation Sensor: www.adafruit.com/product/483
- Evil Mad Scientist Labs Mega Menorah 9000: www.adafruit.com/product/2291

Arduino is a coding environment build on C/C++ and designed for flexibility and ease of use, but it can still seem daunting to first-time users. Practically, the OpenCTD source code is complete and most users will only need to make small alterations to 3 lines of code during assembly and testing, but it is extremely beneficial to understand what the software is doing. Calibration and troubleshooting will require users to load different programs onto the completed OpenCTD. Basic familiarity with the Arduino Integrated Development Environment (IDE) is essential. Environmental Monitoring with Arduino: Building Simple Devices to Collect Data About the World Around Us is a short, easy to understand, introduction to the Arduino ecosystem, and will provide you with many ideas for expanding your inventory of open-source environmental sensors.

- Environmental Monitoring with Arduino: https://amzn.to/2M17yUi

1.2 Project Status

OpenCTD is stable (as of 4/22/2019) on the ATSAMD21G18 ARM Cortex M0 processor. Construction workflow, as well as pinouts, bill of materials, and operation are designed around the Adafruit Adalogger M0. Adjustments may need to be made to adapt to other M0-based microcontrollers.
An older version of OpenCTD is stable on the ATMEGA32U4 processor common to many Arduino systems. Construction workflow, as well as pinouts, bill of materials, and operation are designed around the Qduino Mini. Adjustments may need to be made to adapt to other ATMEGA32U4-based microcontrollers.

1.3 Field Trials

Field trials are critical to assessing the precision, accuracy, durability, and functionality of the OpenCTD. Essential data from field trials are archived online in the OpenCTD GitHub repository.

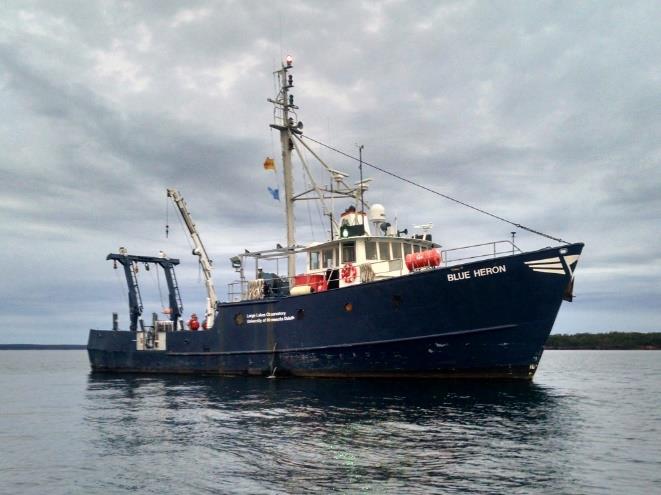
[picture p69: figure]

Lake Superior, R/V Blue Heron: Initial field trials were completed in October of 2015 and analysis of the data from the first several casts confirmed the accuracy of OpenCTD compared against a commercial CTD. OpenCTD was successfully deployed to a depth of 140 meters. This initial field trial, supported by a UNOLS grant to Andrew Thaler, tested the earliest version of the OpenCTD, which still used mineral oil for pressure compensation and was conducted in a freshwater lake, so did not test the conductivity probe. All data and field notes from the first Field Trial can be found in the Blue Heron 15-11 repository.

Gloucester Point, VA, Hurricane Hermine: Hurricane Hermine is a tropical cyclone that passed over our field site in coastal Virginia on September 4, 2016. To test the longevity of the batteries and the durability of the OpenCTD during long term deployments, Andrew Thaler placed two units in our Test Ditch (a tidally influence drainage ditch connected to the Mobjack Bay estuary), where they remained for 74 hours. This field trial tested the first generation OpenCTD based on the Qduino Mini Arduino platform. Notes and data files can be found in the HermineDeployment_9-2016 repository.

Figure 2. The RV Blue Heron on Lake Superior.

## 2.0 Materials and Preparation

Before beginning the build, you will want to familiarize yourself with the individual components as well as the Arduino Integrated Development Environment. By ensuring that the software is running correctly, and the base components have been assembled and tested, you can save yourself significant frustration down the road. It requires about 6 hours to 3D print all parts, so it is best to have those ready to go before beginning the build. Setting up Arduino from scratch can be a challenging and unintuitive process the first time you do it, so it is a good idea to invest an hour or two into making sure you have compatible, up-to-date libraries and that the OpenCTD code compiles on your computer.
Arduino provides an online development environment if you cannot install software on your personal computer: https://create.arduino.cc/.

2.1 Bill of Materials

The OpenCTD is designed such that it can be assembled entirely from components available from large online electronics vendors such as Adafruit, Sparkfun, Amazon, or AliExpress. Many components can also be purchased directly through their supplier or sourced through auction sites at lower cost. Quality across suppliers for most components has been generally consistent.
Some parts, such as resistors and capacitors, are very cheap but hard to source individually. “Introduction to electronics"-type kits, which include many standard resistors and capacitors in small lots tend to be the most economical choice.
Raw, calibrated absolute pressure sensors are available in both 14-Bar and 30-Bar modules from several vendors. These are surface mounted sensors that require significant soldering skills to mount properly. Beginners may prefer to use the simpler, but more expensive, pressure sensor breakout board. Detailed discussion of the differences and benefits between the two pressure sensor solutions is discussed in Chapter 3.
While we provide a list of recommended parts, these are not necessarily the least expensive option and price can vary significantly depending on local availability and number of units being built. Part availability varies from month to month, and some components may become permanently unavailable or listed under a new manufacturer and product name. We do our best to keep the bill of materials up to date.
If you find any discrepancies, please contact us.

OpenCTD - 9

2.2 Recommended Components
Item | Links | Price
Adafruit Feather M0 Adalogger | https://www.adafruit.com/product/2796
| https://amzn.to/2TPkI5H | $19.95
Adafruit Stacking Header | https://www.adafruit.com/product/2830 | $1.25
Adafruit DS3231 Precision RTC FeatherWing | https://www.adafruit.com/product/3028
| https://amzn.to/2CRMjgY | $13.95
CR1632 3V Coin Cell Battery | https://amzn.to/2IQ9dZS
| https://www.adafruit.com/product/380 | $6.99
MS5803-14BA Pressure Sensor Breakout | https://www.sparkfun.com/products/12909
| https://amzn.to/2TTEih2 | $59.95

Alternative Pressure Sensor Assembly
MS5803-14BA Pressure Sensor | https://www.newark.com/sensor-solutions-te-connectivity/ms580314ba01- | $21.82
00/pressure-sensor-14bar-digital/dp/03AC1591 (https://www.newark.com/sensor-solutions-te-connectivity/ms580314ba01-00/pressure-sensor-14bar-digital/dp/03AC1591)
SOIC to DIP Adapter | https://www.adafruit.com/product/1212
| https://amzn.to/2IPgvNn | $2.95

10 kΩ Resistor
0.1 uF Capacitor
DS18B20 Temperature Sensor in Stainless Steel Housing | https://amzn.to/2YOevug | $8.98
Atlas Scientific Conductivity Circuit | https://www.atlas-scientific.com/product_pages/circuits/ezo_ec.html
| https://amzn.to/2K0Xk5z | $60.00
Atlas Scientific Conductivity Probe | https://www.atlas-scientific.com/product_pages/probes/ec_k1-0.html
| https://amzn.to/2K0Xk5z | $139.00
SanDisk MicroSD Memory Card | https://amzn.to/2FTkfKW | $4.99
Lithium Ion Battery Pack 3.7V 4400 mAh | https://www.adafruit.com/product/354
| https://amzn.to/2IfxuIF | $19.95
Lithium Ion Battery Pack 3.7V 2000 mAh | https://www.adafruit.com/product/2011
| https://amzn.to/2UOLmkq | $12.50
2” PVC | https://amzn.to/2JZnNAm | $5.22
Oatey 270229 End of Pipe Gripper Mechanical Plug | https://amzn.to/2WLCcS7 | $5.91
10 kΩ Resistor (2)
4.7 kΩ Resistor (1)
Adafruit Perma-Proto Small Mint Tin Size Breadboard PCB | https://www.adafruit.com/product/1214 | $7.95
Right Angle Female PCB Header | https://amzn.to/2ICUOki | $9.18
Breakaway Male PCB Header
10mm X 3mm Round Rare Earth Magnet (2) | https://amzn.to/2XGbUS3 | $9.90
10mm round double-sided adhesive | https://amzn.to/2XB0kY8 | $6.90

2.3 Tools and Consumables

Tools for general electronics work: flush cutters, wire stripper, soldering iron, solder tip cleaner, helping hands, needle-nosed pliers, utility knife, forceps, solderless breadboard, heat gun.
Consumables for general electronics work: lead-free solder, desoldering braid, electrical tape, 22-gauge solid core wire, 20-gauge copper hook-up wire, heat shrink tubing (various small sizes).

Tools for 3D printing: 3D printer, deburring tool.
Consumables for 3D printing: Filament.

Tools for housing and adhesion: Hand saw or PVC pipe cutter, drill with 1” bit or router and jig, 3M epoxy gun for 50ml cartridges (https://amzn.to/2USjGv8), hot glue gun.
Consumables for housing and adhesion: LOCTITE Adhesive Epoxy (Hysol EA-90FL), venturi mixing nozzles for 50 mL epoxy cartridges, Loctite Epoxy Five Minute Instant Mix, hot glue, super glue, sandpaper.

Tools for Arduino programming: Computer capable of running Arduino IDE, micro-USB cable, coffee maker.
Consumables for Arduino programming: Calibration standard for conductivity, coffee.

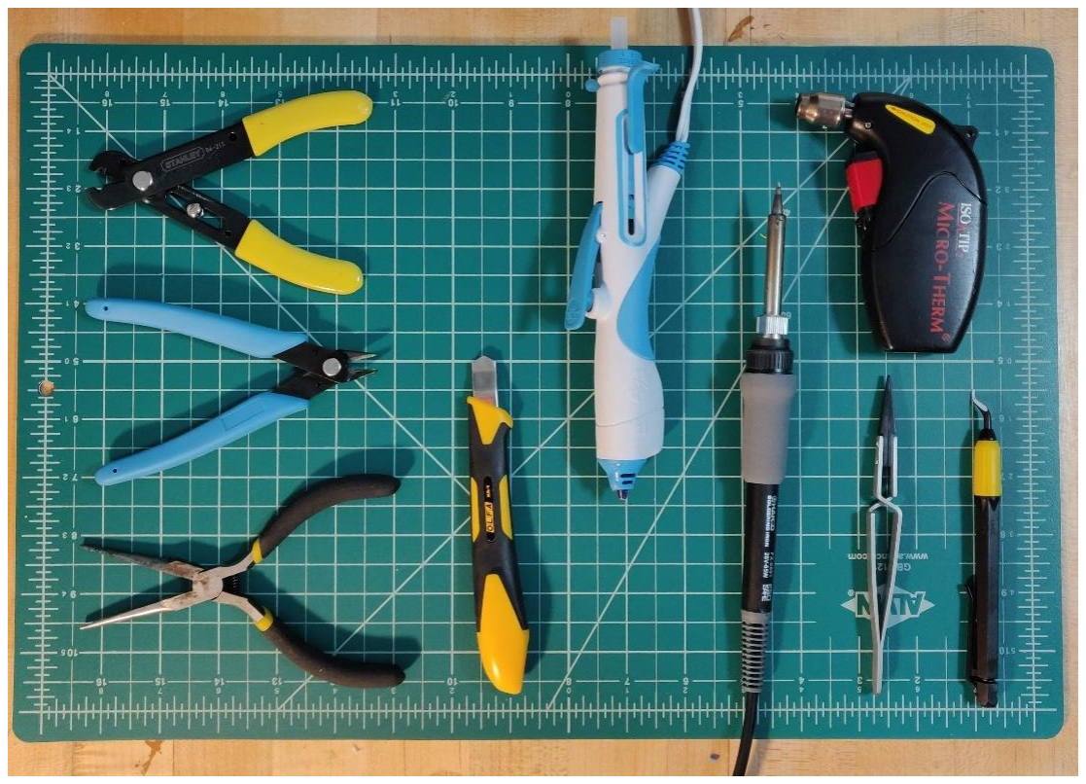
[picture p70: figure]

Figure 3. Most of the tools needed to construct an OpenCTD.

2.4 3D-Printing

The main support structure as well as the sensor baseplate, magnetic switch and connector reinforcement are 3D-printable objects. While it is possible to construct a fully functional OpenCTD without using these parts, they are designed to make building and operating the device simpler and more intuitive. The primary parts are: the electronics chassis which holds the Adalogger and other electronic components, allowing users to easily access the SD card while minimizing strain on the wiring; the sensor baseplate which provides a foundation and template for arranging the sensors prior to potting them in epoxy; the 3-part magnetic switch, which allows users to turn the OpenCTD on and off without opening the housing; and the sensor hub connector, which helps relieve strain on the sensor connection when plugging and unplugging the sensors from the electronics. A second sensor baseplate is also provided for use with the pressure sensor breakout board. If you use the Sparkfun Breakout Board for the pressure sensor, print the OpenCTD_Baseplate_Sparkfun_M0.stl file.
All parts are designed to be printed in PLA at 100-micron resolution with 10 to 20% infill. Only the electronics chassis and magnetic switch (internal) requires support structures.

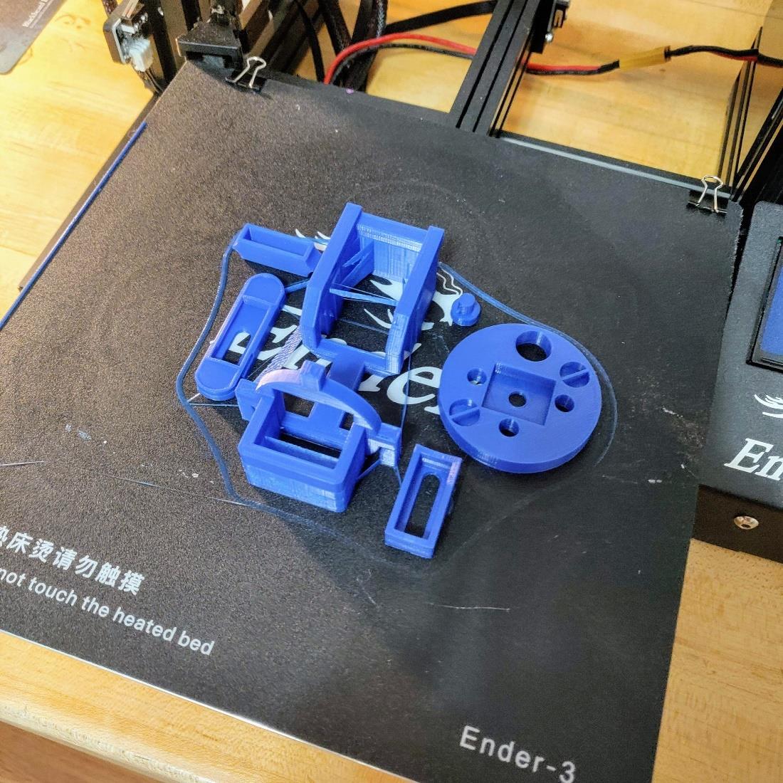
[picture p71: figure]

Figure 4. All of the components can be 3D-printed in a single batch in about 5 hours, with support for the chassis and magnetic switch (internal) only.

OpenCTD 3D Printed Structural Components:

- Baseplate: OpenCTD_Baseplate_M0.stl
- [ALT] OpenCTD_Baseplate_Sparkfun_M0.stl
- Electronics Chassis: OpenCTD_ElectronicsChassis_M0.stl
- Connector: OpenCTD_Connector_M0.stl
- Magnetic Switch (external): OpenCTD_MagneticSwitch_External_M0.stl
- Magnetic Switch (internal): OpenCTD_MagneticSwitch_Internal_M0.stl
- Magnetic Switch Pin: OpenCTD_MagneticSwitch_Pin_M0.stl

OpenCTD 3D Printed Auxiliary Components:

- Jig for aligning notches in PVC pipe: 2-inch_PVC_NotchJig.stl
- Cap for sealing the top during painting: 2-inch_PVC_PaintCap_Top.stl
- Cap for sealing the bottom and protecting sensors during painting and transport: 2-inch_PVC_PaintCap_Bottom.stl

Once the sensor baseplate is complete, use a deburring tool to round of all the edges on both top and bottom as well as inside each hole. Sensors, especially the pressure sensor, should fit snuggly inside their respective hole and the entire baseplate should fit tightly into a 2” PVC pipe. Additional parts are available to simplify assembly, including a marking jig for lining up the bottom slot in the PVC and two caps to cover the sensors and top opening when painting the CTD.

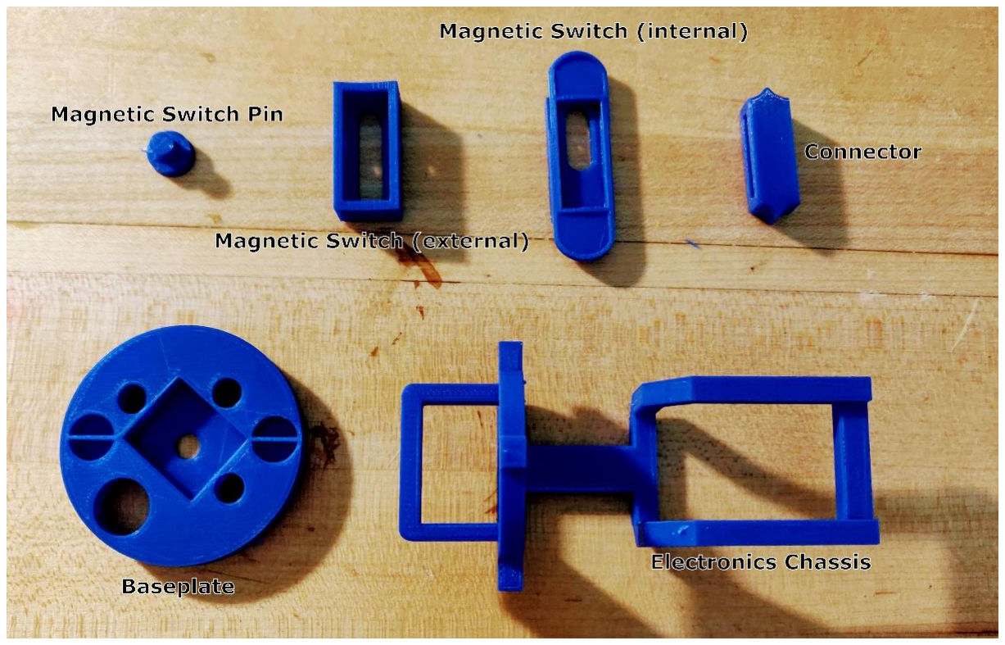
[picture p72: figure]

Figure 5. 3D Printed parts for OpenCTD.

2.5 Preparing the Adalogger and RTC

Skills: Soldering
Parts: Adafruit Feather M0 Adalogger, Adafruit DS3231 Precision RTC FeatherWing, Standard Headers, Stacking Headers, CR1220 Coin-cell Battery
Consumables: Solder

Both the Adalogger and RTC will need headers. Headers are the pin (male) or slot (female) assemblies that allow you to connect and disconnect electronic components while guaranteeing solid electrical contact. Assembling the Adalogger and Real-Time Clock (RTC) is a great, low-risk, opportunity to practice your soldering skills. The Adalogger will receive stacking headers—headers that contain both make and female ends so that board can be connected to a breadboard while a second device (in this case the RTC) can be mounted on top. The RTC will receive male headers facing down so that they can be connected to the Adalogger.

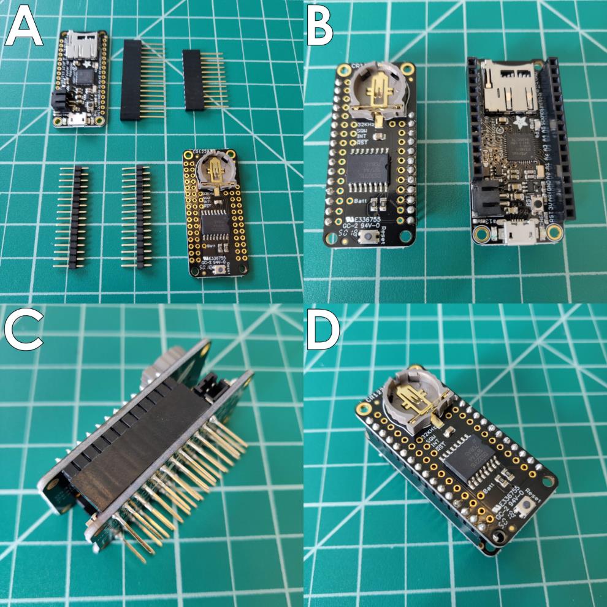
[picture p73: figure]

Figure 6. Adalogger and Real-time Clock with associated headers (A); after soldering (B); connected in profile (C); connected from above (D).

1. Slot the stacking headers into the through-holes on the Adalogger, ensuring that the number of pins matches the number of available holes. The female side of the stacking headers should face up.
2. Flip the Adalogger over so that male pins are facing up. Ensure that the headers are square and perpendicular to the face of the Adalogger.
3. Solder the four corner pins, double check that the headers are straight, and then solder the remaining pins.
4. Slot the male headers into the outer through-holes of the RTC such that the short ends pass through the board and are facing up.
5. Solder the four corner pins, double check that the headers are straight and aligned with female headers on the Adalogger and solder the remaining pins.
6. Insert the CR1220 battery into the RTC.

2.6 Software and Libraries

Skills: Software Management
Parts: Your Computer, Adalogger, SD Card, micro-USB cable
Consumables: N/A

In order to prepare your computer to talk to the Adalogger, download and install Arduino IDE (https://www.arduino.cc/en/Main/Software). You will need to install additional boards so that Arduino IDE will be able to recognize the Adalogger. For a detailed walkthrough of this process, with screenshots included, please visit: https://learn.adafruit.com/adafruit-feather-m0-adalogger/setup (https://learn.adafruit.com/adafruit-feather-m0-adalogger/setup)
We use GitHub to host various projects. GitHub can seem a bit daunting to people who aren’t familiar with it. At its core, GitHub is a tool to organize files, coordinate files, and maintain version control (multiple people can edit the same file, while keeping everything in sync). Projects are organized into repositories (‘repos’) that contain the source code, supporting documents, data files, and other materials needed for each project. When you visit a repo, check the README.md, this will generally describe the project (including the current status), contain necessary guides, and let you know how to contribute.
1. Under preferences, in the File menu, add the following URL to the
“Additional Boards Manager URLs” field: https://adafruit.github.io/arduino-board-index/package_adafruit_index.json (https://adafruit.github.io/arduino-board-index/package_adafruit_index.json)
2. Click “Ok” and then navigate to Tools > Board > Boards Manager.

3. In Boards Manager, search for “Adafruit SAMD Boards” and install the library. Now search for “Arduino SAMD Boards” and install this library as well.
4. Reboot Arduino IDE.
5. When Arduino IDE restarts, you should see several new Adafruit options in the Board menu. The Adalogger is an Adafruit Feather M0 with an embedded SD card reader. Select “Adafruit Feather M0” from the menu.
6. Create an empty text file call datalog.txt on the SD card and insert it into the Adalogger’s SD card reader.
7. Connect your Adalogger to your laptop using a micro-USB cable. The necessary drivers should automatically install.

2.6.2 Required Arduino Libraries

The following Arduino libraries are required for the OpenCTD and come packaged with Arduino IDE by default:

Wire. For communicating with I2C devices like the pressure sensor.
SPI. Serial Peripheral Interface for communicating with a standard SD card reader. SD. For reading and writing to a standard SD card reader.

The remaining libraries you will need to download and install manually. Please refer to https://www.arduino.cc/en/Guide/Libraries for detailed instructions for installing libraries.

MS5803_14. For the MS5803 14 Bar pressure sensor. Download this library here: https://github.com/millerlp/MS5803_14 (Note: if you decide to use a different pressure sensor, you will need to update this library).
Dallas Temperature Control. Allows you to communicate with the DS18B20 thermometer. Download this library here: https://github.com/milesburton/Arduino-Temperature-Control-Library. OneWire. For controlling the Dallas 1-wire family of devices, which includes the temperature sensors. Download the library here: https://github.com/PaulStoffregen/OneWire.
RTClib. For controlling and reading the Real-time Clock. Download the library here: https://github.com/adafruit/RTClib.

The final library is a bit more complicated. The standard SoftwareSerial library is not compatible with SAMD microcontrollers like the Adafruit Feather M0. An updated library is available from the main Arduino branch, but it also requires modification to work with the Adalogger. The updated, functional library can be found here:

https://github.com/OceanographyforEveryone/OpenCTD/tree/master/OpenCTD_Feather_Adalogger/Support_Code/SoftwareSerial (https://github.com/OceanographyforEveryone/OpenCTD/tree/master/%20OpenCTD_Feather_Adalogger/Support_Code/SoftwareSerial)

You can confirm that your set-up is correct by loading the OpenCTD_master_m0.ino Arduino sketch into Arduino IDE, setting the board to Adafruit M0, and pressing “Verify”. If the program compiles without error, make sure your Adalogger is connected and press “Upload”.

2.7 Preparing the housing

Skills: Hand tools
Parts: PVC Pipe, 3D-printed spacing jig (optional)
Consumables: N/A

To create the housing, you’re cutting a short length of schedule-40 2” PVC pipe and adding notches to one end of it. These will allow water to flow over the sensors while protecting them from impacts and entanglement.

1. Cut a 12” section of PVC pipe and deburr the edges.
2. Use the 3D-printed jig to mark four spots where the notches will go.
3. If you have access to a router table, cut 4 1” deep notches into one end of the PVC using a ½” bit. If you have access to a drill and bit, cut 3 1” holes as close to the base as possible on one end.

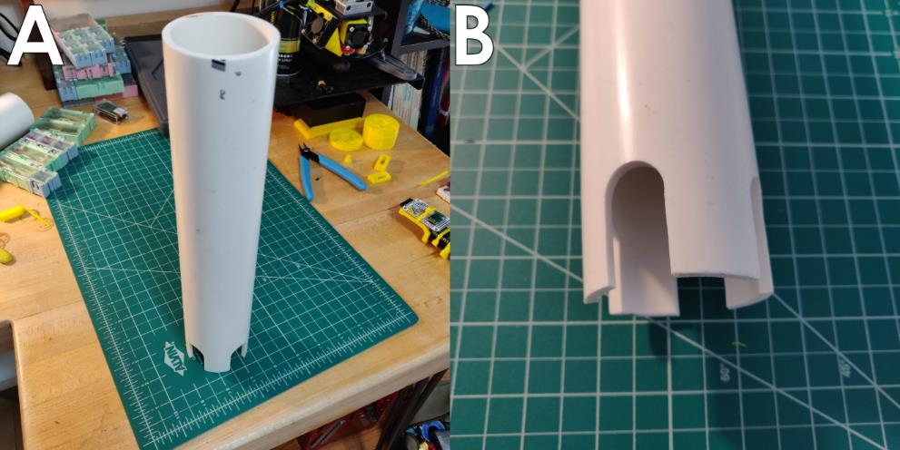
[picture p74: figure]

Figure 7. 12" PVC pipe (A) with notches cut at the base (B).

## Benchmark 1: Confirm Software Install and Adalogger/RTC assembly

Test the Adalogger and real-time clock to confirm that they are working correctly by loading the OpenCTD software onto the Adalogger and using the serial monitor within Arduino IDE to confirm that the software is working correctly. The SD card must be inserted. You should see the date and time, followed by a series of zeros, since there are no sensors connected to read.

Checklist:

- Adalogger connects to PC.
- OpenCTD software compiles and uploads to Adalogger.
- Serial monitor connects and can read data.
- Real-time clock shows the correct time.

## 3.0 Sensor Assembly and Breadboard Testing

The OpenCTD uses three separate types of sensor to accurately and precisely measure the marine environment. The pressure sensor is a MS5803-14BA built by Measurement Specialties and is accurate to 1cm when properly calibrated. The pressure sensor also includes an on-chip thermistor; however, the onboard thermistor is very slow and is unused. For custom builds with extremely limited space that don’t need the device to reach equilibrium relative quickly, users can opt to read temperature directly from the pressure sensor. The standard OpenCTD uses a battery of three DS18B20 thermistors sealed in a stainless-steel housing to take a temperature average of the ambient environment. Finally, the OpenCTD uses a commercially available Atlas EZO conductivity system consisting of a probe and conductivity circuit to determine salinity.

3.1 Pressure Sensor

Skills: Soldering
Parts: MS5803-14BA, SOIC8-to-DIP adapter, 100nF (104) capacitor, 10kOhm pull-up resistor Consumables: Solder, solid-core wire

To build the pressure sensor, you will need to surface mount the pressure sensor chip onto an SOIC8-to-DIP adapter. This is the most challenging solder step in the entire build and requires a steady hand. The pressure chip is able to withstand high heat for a short amount of time, as long as there is no direct contact. Be extremely careful not to touch the gel covering the pressure sensor.

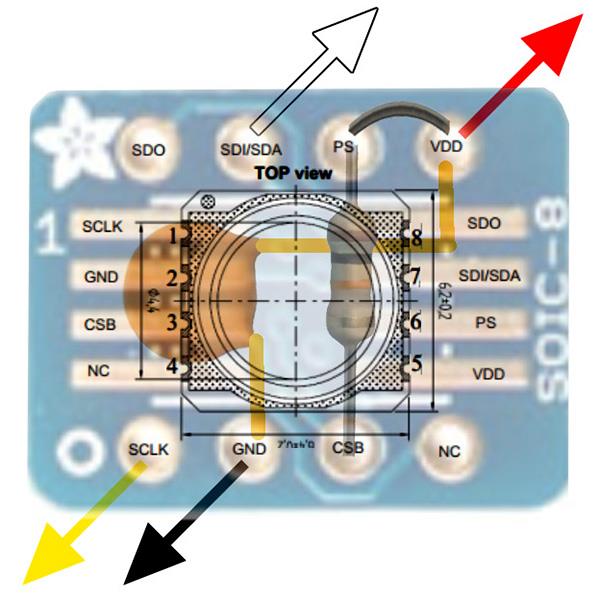
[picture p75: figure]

Figure 8. Diagram of pressure sensor chip and component alignment on SOIC-8 to DIP adapter. Note alignment of pin 1 on the chip to the alignment indicator (in this case, the Adafruit star, but on most boards simply a dot). Image courtesy of the Cave Pearl Project, who have an excellent guide to using and soldering these little chips here: https://thecavepearlproject.org/2014/03/27/adding-a-ms5803-02-high-resolution-pressure-sensor/).

1. Make sure that side of the SOIC8-to-DIP adapter with the larger pads is facing up. Add a small amount of solder to each pad.
2. Ensure that the dot and notch on the pressure sensor line up with the dot on the SOIC-to-DIP adapter. Solder the sensor in place by applying a small amount of solder to the vertical grooves and drawing it down onto the solder pads. Be careful not to short any connections.
3. Flip over the adapter and solder a 10kOhm pull-up resistor between pin 3 and 6.
4. Solder the 100nF (104) capacitor between pins 2 and 5, then bridge pins 5 and 6 with a short wire or with a solder bridge.
5. Solder a 6 cm length of solid core wire to pin 1 (SCL), pin 2 (ground), pin 5 (VCC), and pin 7 (data). Keep track of which wire goes to which pin by color-coding each pin (we recommend red for VCC; black for ground; yellow for SCL; and blue for data).

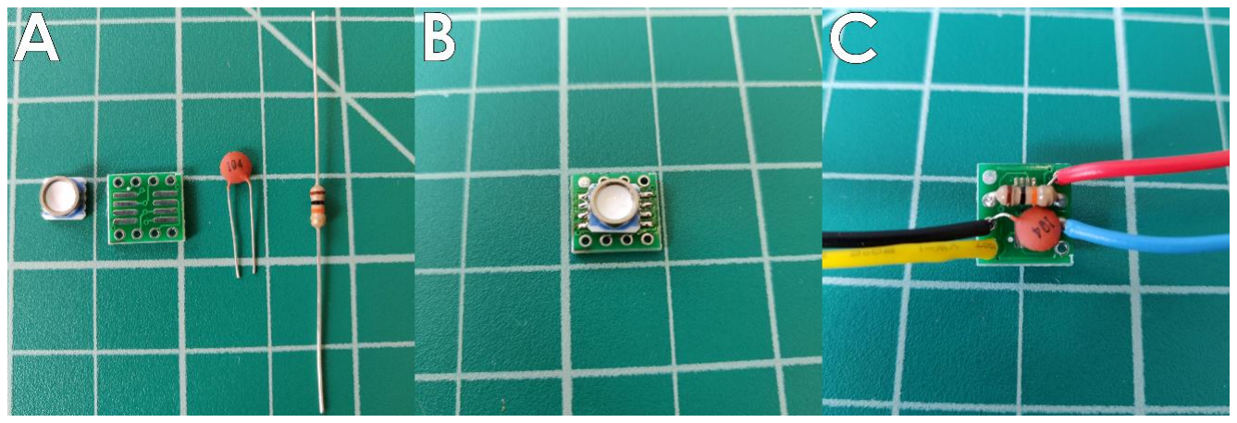
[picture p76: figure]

Figure 9. Building the Pressure Sensor unit. A: Components of the sensor. B: Surface mounting the sensor. C: Wiring up the components.

6. ALTERNATIVE: If you’re using the Sparkfun Pressure Sensor Breakout Board, solder a 5 cm length of solid core wire to SCL, GND, VCC, and SDA. Keep track of which wire goes to which pin by color-coding each pin (we recommend red for VCC; black for GND; yellow for SCL; and blue for SDA).

3.2 Temperature Sensors

Skills: Soldering
Parts: DS18B20 thermistors

Consumables: Solder, heat shrink tubing, solid-core wire

The OneWire protocol allows multiple digital sensors communicate through a single signal, so we can connect all the thermistors to a shared data pin in the Adalogger. In preparing these sensors, our objective is to join the three units together with as little excess wire as possible but with enough slack that moving and positioning the probes do not put any extra stress on the solder joins.

1. Cut the wire on each temperature probe approximately 10 cm from the probe-end terminus and strip half a centimeter of insulation from each wire,
exposing the metal strands.
2. Twist all three black wire strands together and solder. Do the same for the red and yellow wires, respectively (the colors may vary based on manufacturer, but the important thing is to ensure that matching colors are bundled in sets of three).
3. FOR TESTING Solder a short length of solid core wire to each trio and seal with heat shrink tubing such that any expose contacts are covered.

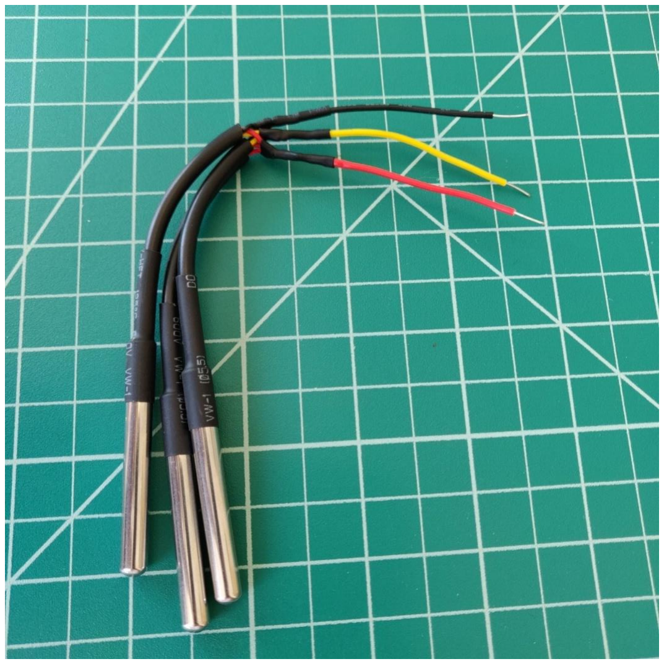
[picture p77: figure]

Figure 10. Temperature probes prepared for testing.

3.3 Conductivity Sensor

Skills: Soldering
Parts: Atlas K 1.0 conductivity probe
Consumables: Solder, solid core wire

The Atlas conductivity probe and EZO circuit need very little preparation prior to testing. If your Atlas kit came with a BNC connector, no additional preparation is required prior to Benchmark 2, however you will have to do step 1 after breadboarding.

1. Cut the probe wire about 4 cm above the probe-end terminus and use a utility knife to strip and expose half a centimeter of wire. The wires may be embedded in extruded insulation rather than simply wrapped and will require a bit of care to extract without damaging the internal insulation.
2. FOR TESTING Solder a short length of solid core wire to each line and seal with heat shrink tubing.

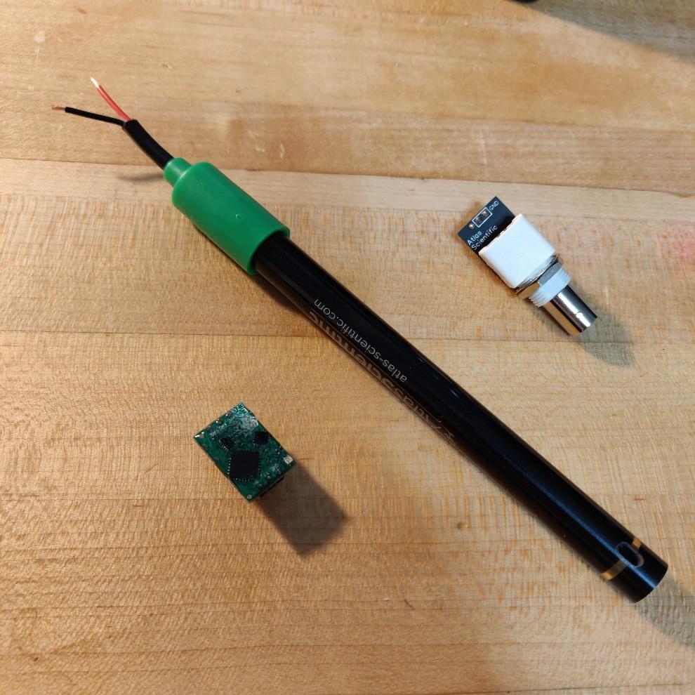
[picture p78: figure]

Figure 11. Conductivity probe with stripped lead wires, Atlas EZO conductivity circuit, BNC connector for simplified testing.

## Benchmark 2: Breadboarding the Circuit

A breadboard is a tool that allows you to prototype an electronic circuit without permanently affixing components. A breadboard is an electronic pegboard with three major regions. The two strips on either side of the board are the ground a positive rail. They are connected vertically. The rails in between are for affixing components. They are connected horizontally and usually clustered in groups of 5. In the center of the breadboard is a dividing groove. Horizontal rails are not connected across the groove. This allows you to mount large components with pins on either side of the central groove, like, for example, an Adalogger. By breadboarding the circuit first, you can ensure that the system is working properly before continuing.

1. Reference Figure 9 and the photo and pinout guide below. Place Atlas EZO circuit and connect jumper wires in accordance.
2. Connect a 4.7 kΩ resistor between pin D6 and the positive voltage rail.
3. Connect a 10 kΩ resistor between the SDA pin and the positive voltage rail and connect a 10 kΩ resistor between SCL pins and the positive voltage rail.
4. Connect the temperature sensors to digital pin 6, positive, and ground.
5. Connect the pressure sensor to SCL, SDA, positive, and ground.
6. Connect the temperature probe to the two probe pins on the Atlas EZO. It does not matter which wire goes to which probe pin. Make sure the conductivity probe itself is connected and sitting in water or it will read zero.
7. Connect the Adalogger to your PC using a micro-USB cable and open the serial monitor in Arduino IDE.
8. Power the Adalogger down, remove the SD card, and read the data file.

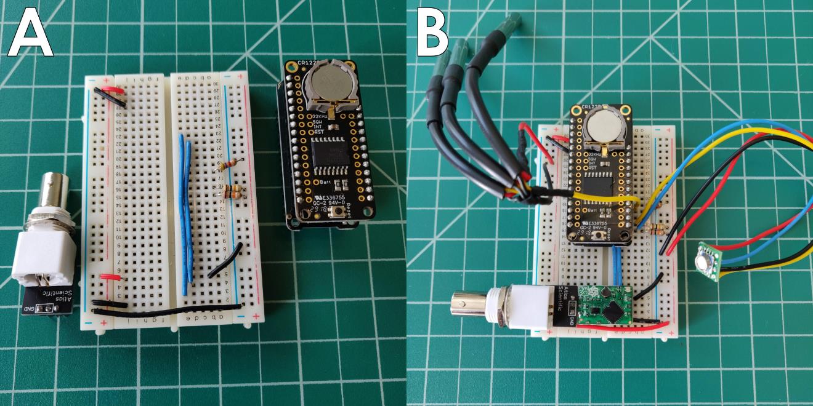
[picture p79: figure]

Figure 12. Breadboard with just jumper wires and resistors attached (A) and with all components (B).

Checklist

- Atlas EZO circuit is blinking with alternating between green and blue lights.
- Temperature probes are reading ambient temperature and are reasonably close to each other.
- Pressure sensor is reading atmospheric pressure (it should be around 1012 mbar if you’re near sea level).
- Conductivity sensor is reading the conductivity of whatever fluid it is in.
- Data had been logged to SD Card

Breadboard Diagram

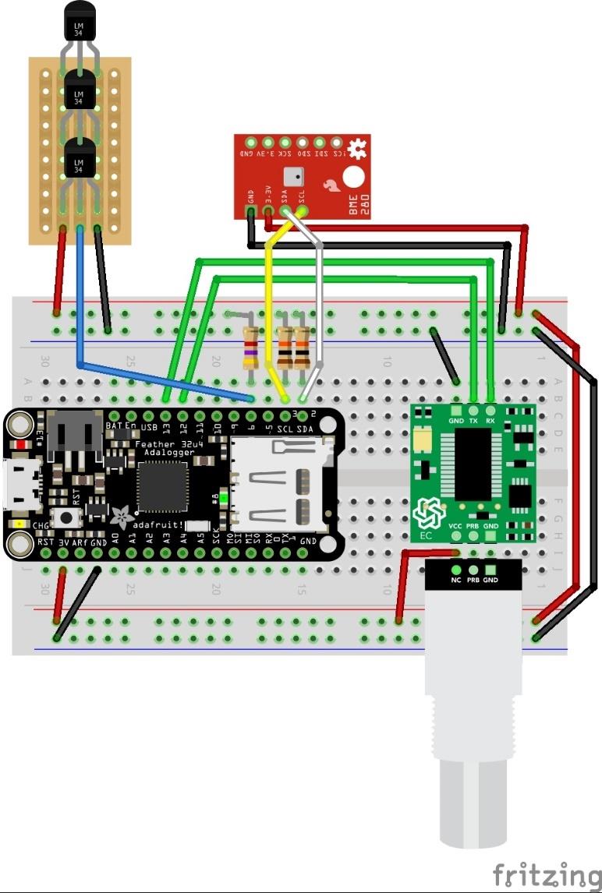
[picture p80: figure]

Figure 13. Diagram of breadboard assembly to test completed sensors. Note the presence of BNC connector for the conductivity probe and the use of a barometric pressure sensor to stand in for the OpenCTD pressure sensor.

## 4.0 Assembling the Main Control Unit

The Main Control Unit is the nervous system of the OpenCTD. It handles all the processing and signal routing between the sensors and the Adalogger. The MCU uses a mint-tin sized permanent breadboard, which is arranged similar to a standard breadboard, but with positive and negative rails in the center of the board and free, unattached pins at either end. This Perma-Protoboard allows you to make permanent electronic connections while mimicking the look and set-up of a breadboard.

4.1 Preparation

Skills: Soldering
Parts: Adafruit Perma-proto board, 8-pin right angle female header
Consumables: Solder

First, we will build the connector that interfaces with the sensors in the OpenCTD housing by attaching an 8-pin, right angle female connector to the end of the Perma-proto board and bridging it to the positive and negative rail with solder.

1. Once the Adalogger has been tested, it no longer needs the long pins that
connected it to the breadboard. Snip these pins off at the base of the Adalogger. The Adalogger should now sit flush inside the Electronics Chassis.
2. Cut 8-pins from a right-angle female header strip.
3. Solder to 8-pin connector to the second to last set of through-holes on the Perma-Protoboard, on the underside such that the pins emerge through the middle column of unconnected through-holes.
4. On the underside of the board, build a solder bridge between the positive and negative strips and their respective, adjacent connector pins. This works best with a soldering iron heated to 750oC. Hotter irons will cause the surrounding solder to melt.
5. ALTERNATIVE: If you have trouble building solder bridges, use small lengths of solid core wire to jump the contacts.

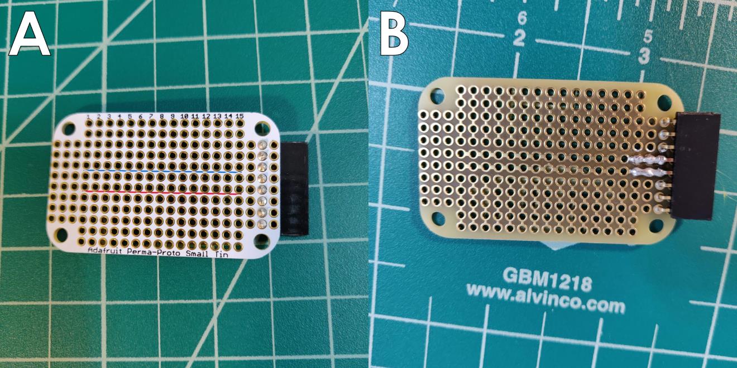
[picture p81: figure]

Figure 14. Perma-Protoboard with 8-pin connector top (A) and bottom, with solder bridges (B).

4.2 Soldering the RTC

Skills: Soldering
Parts: Adalogger/RTC, Adafruit Perma-proto board
Consumables: Solder, solid core wire

Solid core wire will be connected to pass-through holes on the RTC and soldered underneath so that the wires pass between the RTC and the Adalogger and then contact the appropriate pins on the MCU. It is easiest to start with long lengths of wire and cut down to appropriate sizes as you proceed.

1. Connect red and black solid core wire to the 3.3V and GND pins on the left side of the RTC.
2. Place the complete Adalogger/RTC assembly into the Electronics Chassis and stretch these two wires until the meet the end of the Chassis.
3. Cut the wires at the end of the chassis and strip off half a centimeter of insulation from the terminal ends.
4. Solder these two wires to the positive (3.3V) and negative (GND) rails of the Perma-Protoboard along columns 5 or 6.
5. Check the fit by placing the entire unit in the Electronics Chassis. The Adalogger and the Perma-Protoboard should sit flush against their respective support structures.

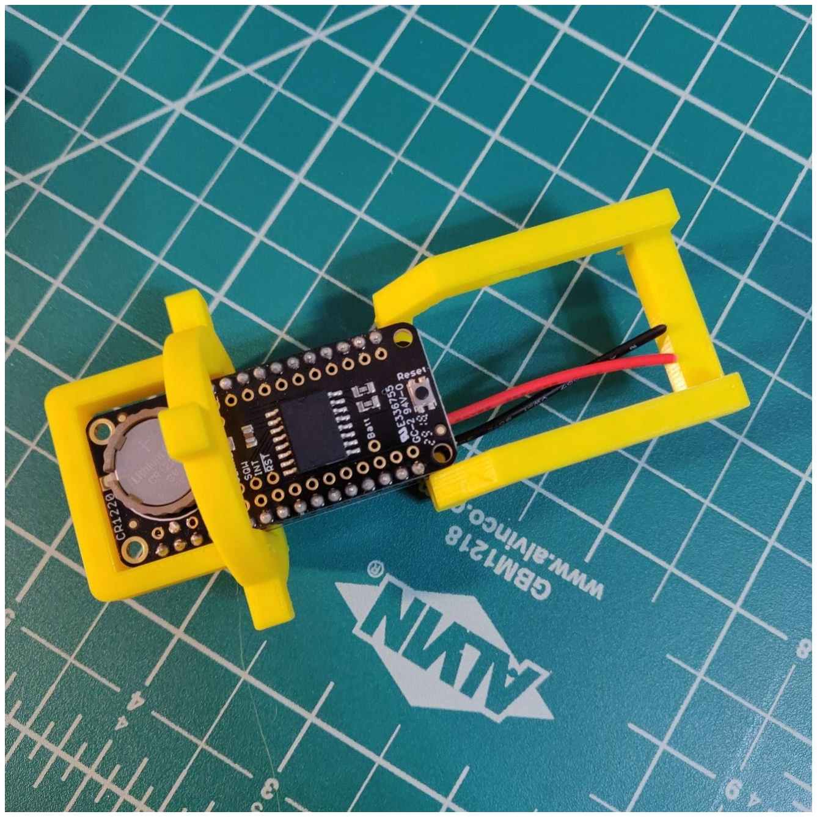
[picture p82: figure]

Figure 15. The Adalogger/RTC with positive and negative wires stretched to their appropriate length.

4.3 Populating the Perma-Protoboard

Skills: Soldering
Parts: Adalogger/RTC, Adafruit Perma-proto board, Atlas EZO circuit, 10 kOhm pull-up resistor (x2), 4.7 kOhm pull-up resistor
Consumables: Solder, solid-core wire

These steps will fully populate the MCU with all necessary components for the OpenCTD. We advise laying out all components first and double checking their placement before soldering. Reference Figures 12 and 13 frequently during assembly.

1. Solder the Atlas EZO circuit to columns 1 through 3 on the Perma-protoboard such that the GND and VCC pins correspond to the correct power rails. Holding the board so that “Adafruit Perma-Proto Small Tin” is correctly oriented, GND/TX/RX should be on top and VCC/PRB/PRB should be below.
2. On the underside of the Perma-proto board, bridge the GND pin to the negative rail with solder.
3. On the underside of the Perma-proto board, bridge the VCC pin to the positive rail with solder.
4. Using solid core wire, connect pin 12 on the RTC to TX on the Atlas EZO.
5. Using solid core wire, connect pin 13 on the RTC to RX on the Atlas EZO.
6. Connect each PRB pin to the through holes adjacent to pins 7 and 8 on the 8-pin header. It does not matter which PRB pin connect to which of the two header pins.
7. Connect the 4.7 kOhm pull-up resistor to column 9, bridging the positive rail and the upper line of 5 connected pins.
8. Using solid core wire, connect pin 6 on the RTC to upper column 9 on the Perma-proto board.
9. Using solid core wire, connect upper column 9 on the Perma-proto board to the through hole adjacent to pin 1 on the 8-pin header.
10. Connect a 10 kOhm pull-up resistor to column 11 and 12 , bridging the positive rail and each upper line of 5 connected pins. If you’re worried about bridging these two resistors, leave an extra column between them.
11. Using solid core wire, connect the SCL pin on the RTC to upper column 11 on the Perma-proto board.
12. Using solid core wire, connect upper column 11 on the Perma-proto board to the through hole adjacent to pin 2 on the 8-pin header.
13. Using solid core wire, connect the SDA pin on the RTC to upper column 12 on the Perma-proto board.

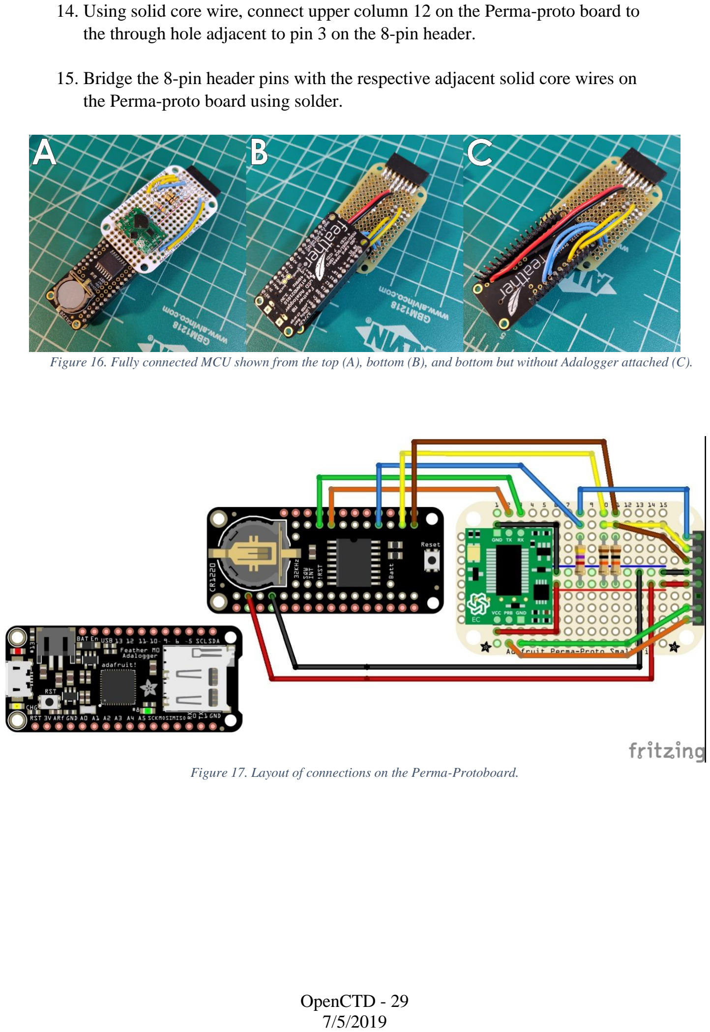
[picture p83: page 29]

14. Using solid core wire, connect upper column 12 on the Perma-proto board to the through hole adjacent to pin 3 on the 8-pin header.
15. Bridge the 8-pin header pins with the respective adjacent solid core wires on the Perma-proto board using solder.

Figure 16. Fully connected MCU shown from the top (A), bottom (B), and bottom but without Adalogger attached (C).

Figure 17. Layout of connections on the Perma-Protoboard.

## Benchmark 3 – Testing the Master Control Unit

Prior to potting sensors in epoxy, this test will ensure that the Master Control Unit has been assembled correctly and that all sensors are being read. Once you confirm that the MCU functions correctly you will be ready to move on to the final phase of the OpenCTD build. You will connect each sensor to its appropriate pin on the female connector using the solid core wire already soldered to each sensor assembly.

1. Holding the Perma-Protoboard face up with the connector on the right, the
order of pinouts is, from top to bottom, D6 (Temperature), SCL (Pressure), SDA (Pressure), Ground, 3.3 Volt, UNUSED, Probe (-), Probe (+). Note that, as the conductivity probe functions like a resistor, it does not matter which line from the probe connects to which of the two pins.
2. Connect each sensor to their respective pin. Pressure and Temperature sensors will share a common voltage and ground.
3. Reconnect the Adalogger and check the serial monitor. If all sensors are reading accurately, you’re ready to prepare and pot the sensors.
4. Using zip ties, attach the Adalogger/RTC and Perma-proto board to the 3D-printed MCU frame.

Checklist

- MCU can read pressure sensor when connected.
- MCU can read temperature sensors when connected.
- MCU can read conductivity sensor when connected.

## 5.0 Mounting and Potting Sensors

Potting the sensors is the point of no return. Once they are sealed in epoxy, they cannot be removed. It is essential that you confirm all sensors are operating correctly before final potting. If you have cleared every benchmark, you will be ready to go.

5.1 Baseplate and Potting the Pressure Sensor

Skills: Epoxy Potting
Parts: Pressure sensor, temperature probe, conductivity probe
Consumables: Hot glue, instant epoxy

The 3D printed baseplate provides a template for accurately aligning all five sensors as well as an end-stop to prevent epoxy from leaking out during potting. The pressure sensor sits in the center of the template and fits snuggly into the central hole. This sensor will be potted first with instant epoxy to protect the circuits before the full sensor assembly is potted. Be extremely careful not to get any epoxy on the gel of the pressure sensor.

1. Seat the pressure sensor into the central hole on the side with the large square indentation and ensure that the actual sensor sits flush with the bottom face of the baseplate.
2. Once the sensor is correctly seated, apply just enough instant epoxy to fill the entire rectangular indentation. The epoxy will settle during pouring as it flows under the circuit board.
3. Carefully check that no epoxy is leaking out through the central hole.
4. Let it sit for a 10 to 20 minutes to allow the epoxy to set.


Figure 18. Pressure sensor seated and potted in baseplate.

5. Once the epoxy has set, insert each temperature probe into the three holes such that 1.5 to 2 cm extends out of the bottom of the baseplate.
6. Hot glue each sensor into place, sealing any possible holes. The hot glue will prevent epoxy from leaking out through these pass-through holes during potting.
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

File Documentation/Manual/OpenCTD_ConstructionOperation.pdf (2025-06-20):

# Construction and Operation of the

# OpenCTD

OpenCTD: Construction and Operation - 2 oceanographyforeveryone.com

Construction and Operation of the OpenCTD

Andrew Thaler, with contributions from Russell Neches, S. Kersey Sturdivant, Jeff Branson, Andrea Schmuttermair, Brian Marx, and Allie Wilkinson.

Fifth Edition: June 2025.

Cover Art by Andrew Thaler.

Photographs by Andrew Thaler and Allie Wilkinson unless otherwise noted.
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

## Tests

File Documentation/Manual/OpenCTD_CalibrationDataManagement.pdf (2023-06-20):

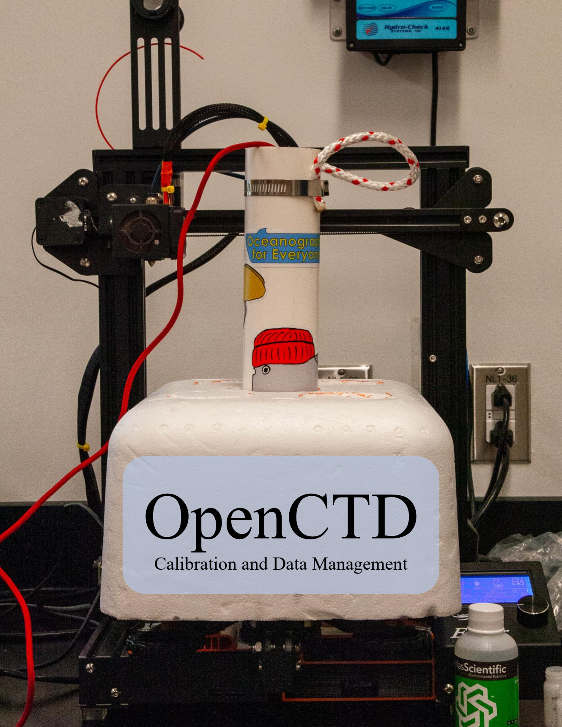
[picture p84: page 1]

OpenCTD: Calibration and Data Management - 1

# OpenCTD

## Calibration and Data Management

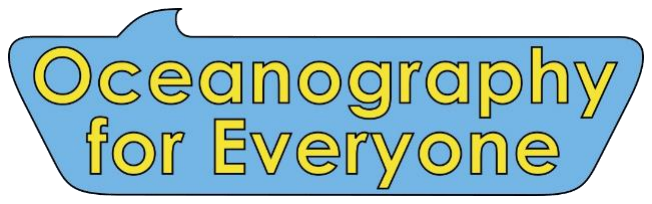
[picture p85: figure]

oceanographyforeveryone.com

OpenCTD: Calibration and Data Management

Andrew Thaler, with contributions from Russell Neches, S. Kersey Sturdivant, Jeff Branson, Andrea Schmuttermair, Brian Marx, and Allie Wilkinson.

First Edition: June 2023.

Cover photo by Allie Wilkinson.

Funding to support the production of this document was provided by a grant from the Open Science Hardware Foundation.

This work is licensed under a Creative Commons Attribution-NonCommercial 4.0 International License. (https://creativecommons.org/licenses/by-nc/4.0/)

## Contents

Introduction to Calibration and Data Management | 4
1 Pressure (Depth) | 5
2 Temperature | 6
3 Conductivity (Salinity) | 8
4 Data Management | 15
5 Additional Resources | 16
Works Cited | 16
Tools and Materials | 16
Sensor Specifications | 16

## Introduction to Calibration and Data Management

The OpenCTD is a low-cost, open-source CTD designed intentionally for budget-restricted scientists, educators, and researchers working in nearshore coastal ecosystems. It was developed by a core team of marine ecologists in collaboration with a distributed community of scientists, engineers, makers, and conservation practitioners. It is assembled from components commonly available at large hardware stores or through major online retailers. An Arduino-based microcontroller controls a battery of sensors sealed within a PVC pipe. Power is provided by a standard 3.7V lithium polymer battery and data are stored in a comma-delimited text file accessed via SD card. All OpenCTD software is released open source with no restrictions on use.

One of the most significant challenges with any open-source scientific instrument is ensuring accurate and precise calibration. Commercial CTDs often require expensive service contracts in order to maintain data quality. The OpenCTD can be calibrated and maintained by the end user, independent of any manufacturer.

While comprehensive validation of OpenCTD calibration requires access to professionally calibrated instruments maintained in a controlled environment, it is not necessary to do a full validation test for every instrument. This level of validation is for those for whom a high degree of confidence and extreme precision are needed. For environmental monitoring, ecology, conservation, management, and most other use cases, an OpenCTD calibrated against salinity standards and general-purpose temperature sensors is adequate.

As the community grows, validated OpenCTDs can be used to benchmark newly built instruments.

A Microsoft Excel and Google Sheets template is available in the OpenCTD GitHub repository. This template will take raw data from the OpenCTD and make the necessary conversions to create human-readable water column profiles.

The GitHub repository for the OpenCTD can be found here: https://github.com/OceanographyforEveryone/OpenCTD

Calibration software, data management templates, and OpenCTD firmware can be found here: https://github.com/OceanographyforEveryone/OpenCTD/tree/main/Software

## 1 Pressure (Depth)

The OpenCTD uses the MS5803 14-bar pressure sensitive chip from Measurement Specialties designed for SCUBA dive watches and depth gauges. This chip contains a pressure sensitive resistor embedded in a gel matrix. The pressure sensor is rated to 140 meters depth. A 30-bar chip, which can double the operating depth of the OpenCTD, is also available, though requires additional customization.


Figure 1. Pressure sensor error versus ambient pressure and temperature for the MS5803-14BA pressure sensor. Provided by manufacturer.

The MS5803 is a factory-calibrated pressure sensor capable of outputting absolute pressure up to 0.2 millibar resolution. No additional calibration is needed by the user. The pressure sensor outputs absolute pressure. At sea level, the average standard atmospheric pressure is 1013.25 mbar, though local weather and small changes in altitude will affect this baseline. To convert pressure in millibars to depth in meters, use the following equation:

D = (P(DEPTH) - P(SURFACE) * 100) / (G * 1000)

Where D is depth in meters; P(DEPTH) is the pressure (in millibars) at depth); P(SURFACE) is the pressure at the surface in millibars; and G is acceleration due to gravity, which for most field purposes can be assumed as 9.81 m/s²
(Fofonoff and Millard Jr, 1983). For high-accuracy and high-resolution commercial CTDs, the latitudinal variation in gravity is considered in the pressure-to-depth conversion as these sensors often offer sub-centimeter accuracy.

For extra accuracy, use the absolute pressure at the surface of the water at the time of deployment by taking the last pressure reading before the conductivity probe contacted the water for P(SURFACE). For deployments in alpine lakes and other high-altitude environments, be aware that surface pressure may be significantly less than 1013.25 mbar.

## 2 Temperature

The OpenCTD uses a DS18B20 digital thermometer potted in a stainless-steel cladding. These sensors communicate over a 1-wire protocol, which allows users to connect multiple sensors to the same data pin. The sensors have an operating range of -55 to 125oC (with peak accuracy between -10 to 85oC). The advertised accuracy is ±0.5oC, however, in field trials using a battery of 3 sensors, we observed mean error as low as ±0.1oC.

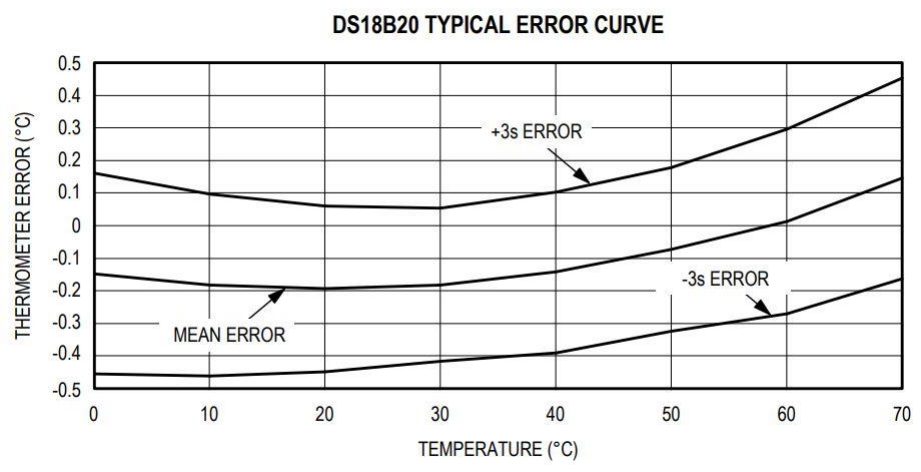
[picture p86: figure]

Figure 2. Typical error curve for DS18B20 digital thermometer. Provided by supplier.

Thermal time constant is a measurement of how quickly the thermistor responds to changes in ambient temperature. It is expressed as the time it takes for a thermistor to cool to 63.2% of the total difference between a stable high temperature and a stable low temperature. We determined the thermal time constant for two different designs of DS18B20 sensors in stainless steel cladding: flat-topped and hemispherical. For sensors clad in a flat top housing, the time constant was 5.7 seconds. For those clad in a hemispherical housing, it was 8.5 seconds.

We also determined equilibration rate for DS18B20 sensors. While equilibration rate is not a precise measurement, it is useful for making quick protocol adjustments in the field and gives a basic guideline for how quickly these sensors react to temperature changes. For transitioning from low temperature to high temperature, the equilibration rate was 1.2 oC/s. For transitioning from high temperature to low temperature, the equilibration rate was 2.3 oC/s.

The DS18B20 digital thermometer is factory calibrated but the user should perform a single-point or two-point calibration in cases where desired precision exceeds the error rate of ±0.1oC. The sensor offset is, however, linear, which means that a single calibration constant can be used to correct the accuracy of the temperature measurements averaged across three sensors. A calibration constant can be established by plotting the average deviation between the OpenCTD temperature sensors and water of known temperature.

Calibrated instruments should remain steady for many casts, but it is always good practice to check your temperature calibration whenever you suspect that the calibration may have changed. We recommend checking temperature calibration at the beginning of each expedition or once per year.

## 3 Conductivity (Salinity)

The OpenCTD uses a graphite conductivity probe manufactured by Atlas Scientific. Electrical conductivity probes are relatively simple devices consisting of two electrodes of known surface area and known distance from each other. As conductive fluid passes between the two electrodes, they measure the resistance of the liquid. The Atlas probe has a response time of 90% within 1 second, a 343-meter maximum operating depth, and a 1 to 110oC temperature range. The K 1.0 probes can measure conductivity from 5 to 200,000 µS/cm.

Salinity is derived following the formulas outlined by the 1978 Practical Salinity Scale (Lewis, 1980). Temperature and pressure are integral parts of this calculation; therefore, it is
recommended that the user use this method for determining salinity instead of using the salinity value derived internally by the Atlas Scientific EZO-EC conductivity circuit. The accuracy of the calculated salinity value ultimately depends on the accuracy of each individual sensor.

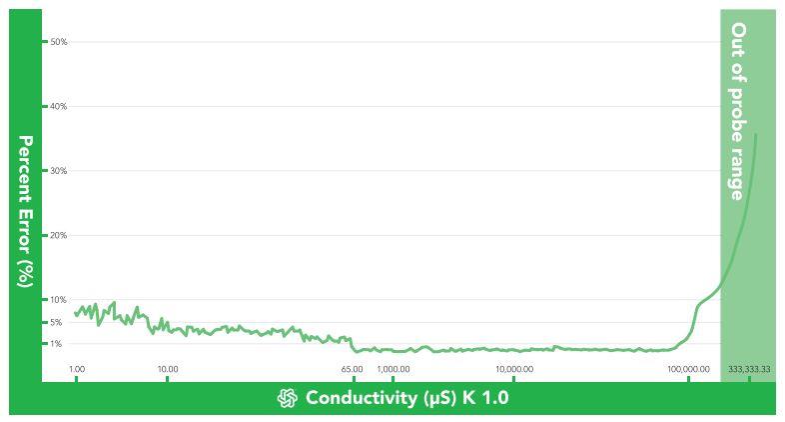
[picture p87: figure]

Figure 3. Accuracy of Atlas Scientific K 1.0 Conductivity Probe and EZO circuit. Data provided by Atlas Scientific.

The conductivity circuit requires a two-point calibration using solutions with a known and precise conductivity. Calibration solutions can be pre-mixed or ordered from a scientific supplier. Atlas Scientific sells a set of conductivity calibration solutions for their probes. Most calibration solutions are designed to be used at 25oC but the Atlas EZO-EC conductivity circuit also allows for temperature compensation if maintaining a stable 25oC temperature is not possible. While any clean glass or plastic container can be used to hold the conductivity solution standards, we recommend a small probe storage bottle to contain the fluid and minimize waste.

Do not return the conductivity solution to the original bottle once it has been used.

In order to clean the conductivity probe and whatever containers you are using to hold the conductivity solution between steps in the calibration process, you will need a source of either distilled water or water filtered through reverse osmosis. Distilled water is readily available in most grocery stores. Reverse osmosis is often used to purify drinking water from seawater and RO machines are often found on oceangoing vessels as well as a component of the filtration system of some high-end ground wells. Aquafina bottled water is produced using reverse osmosis and has no added minerals, making this brand a useful source of RO water.

We have developed a simple system for establishing a controlled, thermally stable environment for the calibration process that uses the hot bed of a low-cost 3D printer, coupled with a Styrofoam cooler, and a large ceramic thermal mass. A few hours before calibration, set the heated bed of the 3D printer to 25oC and prepare the following setup.

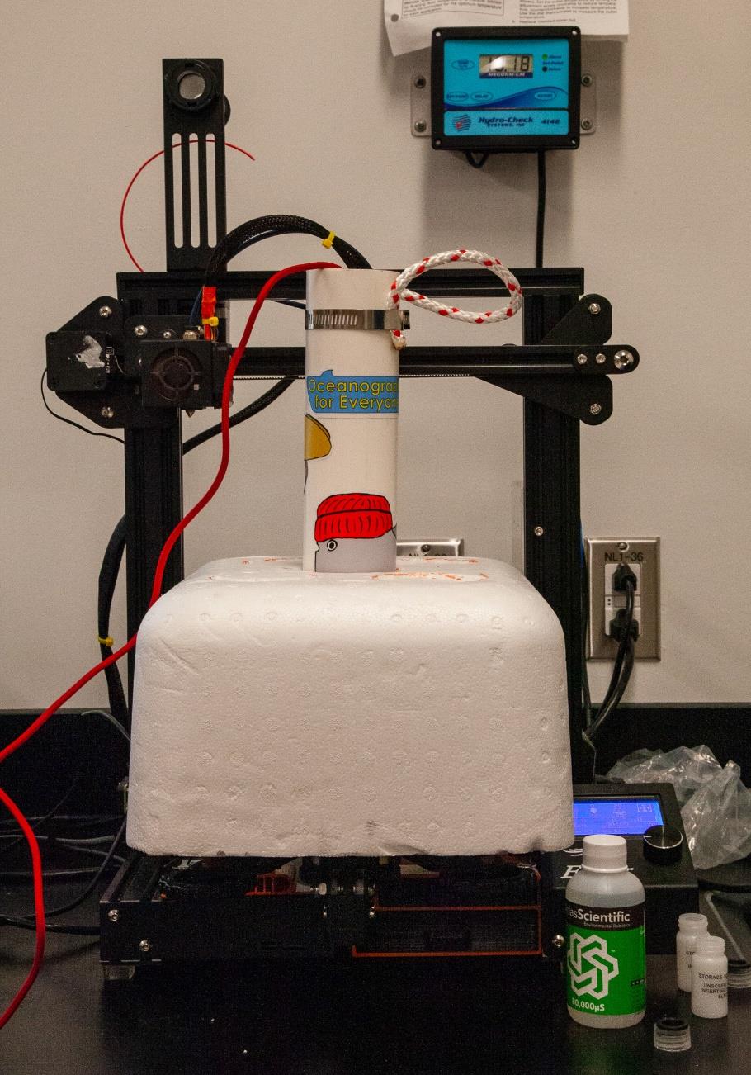
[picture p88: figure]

Figure 4. OpenCTD mounted inside a Styrofoam cooler on top of a 3D printer heat bed in order to maintain an ambient 25oC temperature. Photo by Allie Wilkinson.

Find the largest thermal mass available that the OpenCTD housing can fit inside (a heavy coffee mug works well) and place it on the heated bed of the printer. Cut a hole in the bottom of a Styrofoam cooler large enough for the OpenCTD housing to fit snuggly inside. Place the inverted cooler on top of the 3D printer’s heated bed such that the OpenCTD can be inserted through the hole and sit inside the thermal mass.

When you are ready to calibrate your OpenCTD, insert the device into the hole in the Styrofoam cooler such that it sits inside the coffee mug or other thermal mass, and allow it to reach equilibrium (usually 15 minutes or less).

We have determined through experimentation that even the least expensive 3D printers can maintain a very stable temperature throughout the calibration process. In cases where the ambient temperature is more than 5oC cooler than 25oC, you may want to store the conductivity solution on the heated bed as well. This process will not work for rooms where the ambient temperature is greater than 25oC. Please reference the end of this section for alternatives to temperature compensate the OpenCTD during calibration.

Two-point calibration is facilitated using Serial_for_EC_Calibration_m0.ino (https://github.com/OceanographyforEveryone/OpenCTD/tree/main/Software/Support/Serial_for_EC_Calibration_m0) (https://github.com/OceanographyforEveryone/OpenCTD/tree/main/Software/Support/Serial_for_EC_Calibration_m0) found in the OpenCTD GitHub repository. If only a single calibration standard is available, one-point calibration is possible, but not recommended. This software will also output the average temperature reading from the three temperature sensors.

1. With the control unit powered on and connected to the sensors, upload Serial_for_EC_Calibration_m0.ino to the Adalogger M0. Make sure that the OpenCTD control unit power is also on, as the voltage differential between USB and battery power may affect calibration.
2. Open the serial monitor through the Arduino IDE. Make sure the dropdown menus in the serial monitor are set to “Carriage return” and “9600 baud”. You should see a message with EC Board Info, a note to review this guide, and a reference list of useful commands.
3. Type k,? in the command line and hit enter. This will tell you what the K-value of you probe is set to. It should be set to K=1.0 for most use cases.
a. If the K-value is something other than 1.0 type k,x (where x is the new K-value of the probe) in the command line and hit enter. This is useful if your EZO-EC conductivity circuit reads the incorrect K-value or if you are building an OpenCTD for freshwater deployments using a K 0.1 probe. If there is an error transmitting the command, the serial monitor will report *ER and you should send the command again.

4. To check whether the probe has been previously calibrated type cal,? in the command line and hit enter. If it reads ?CAL,0 the probe has not been calibrated.
5. Type cal,clear and hit enter to clear the previous calibration. It is good practice to send this command even if the circuit reports back that it has not been calibrated. If there is an error transmitting the command, the serial monitor will report *ER and you should send the command again.
6. With the probe dry (be sure there is absolutely no water on the electrodes) enter cal,dry in the command line and hit enter. This will dry calibrate the probe. If there is an error transmitting the command, the serial monitor will report *ER and you should send the command again.
7. Enable continuous monitoring by entering c,1. You will begin to see a steady stream of readings from the conductivity probe updating once per second. If the dry calibration was successful, those values should read 0.00.
8. Clean the probe with distilled or RO water and dry with a clean paper towel. Make sure there is no water trapped in the small hole between electrodes. Clean and dry the probe storage bottle with distilled or RO water and dry with a clean paper towel.

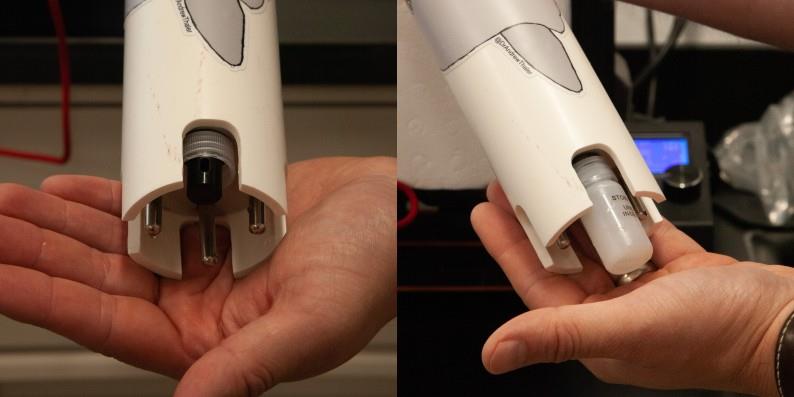
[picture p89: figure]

Figure 5. OpenCTD conductivity sensor with the cap ring of the probe storage bottle placed above the electrode opening (left) and with the conductivity probe completely submerged in the probe storage bottle. Photos by Allie Wilkinson.

9. Fill the probe storage bottle with the less conductive of the two conductivity solutions (12,880 µS if you’re using the Atlas standard solutions). Slide the cap ring of the probe storage bottle onto the conductivity probe so that it sits well above the small hole between electrodes. Slide the probe storage bottle onto the probe and screw it into the cap so that it seals tightly, and the conductivity solution completely covers the small hole between electrodes. Tap the probe gently to shake out any bubbles.
10. Place the probe with the bottle attached in a thermally stable environment. Leave the probe suspended in the conductivity solution until readings stabilize (15 minutes is usually sufficient). The reading should be anywhere from 1% to 40% off from the conductivity solution. Even once they stabilize, there will be small fluctuations in value. If you leave the probe in for too long, it will ionize the water and the conductivity readings will begin to creep up. A gentle shake will return the solution to its baseline.
11. Type cal,low,y (where y is the known value of the standard. If you are using the Atlas conductivity solution, type cal,low,12880) in the command line and hit enter. The conductivity readings in the serial monitor will not update.
12. Remove the probe storage bottle, clean the probe with distilled or RO water, and dry with a clean paper towel. Make sure there is no water trapped in the small hole between electrodes. Clean and dry the probe storage bottle with distilled or RO water and dry with a clean paper towel.
13. Fill the probe storage bottle with the more conductive of the two conductivity solutions (80,000 µS if you’re using the Atlas standard solutions). Slide the cap ring of the probe storage bottle onto the conductivity probe so that it sits well above the small hole between electrodes. Slide the probe storage bottle onto the probe and screw it into the cap so that it seals tightly, and the conductivity solution completely covers the small hole between electrodes. Tap the probe gently to shake out any bubbles.
14. Place the probe with the bottle attached in a thermally stable environment. Leave the probe suspended in the conductivity solution until readings stabilize (15 minutes is usually sufficient). The reading should be anywhere from 1% to 40% off from the conductivity solution. Even once they stabilize, there will be small fluctuations in value. If you leave the probe in for too long, it will ionize the water and the conductivity readings will begin to creep up. A gentle shake will return the solution to its baseline.
15. Type cal,high,y (where y is the known value of the standard. If you are using the Atlas conductivity solution, type cal,high,80000) in the command line and hit enter. The conductivity readings in the serial monitor will update and should read very close to 80,000.

Alternative: For 1-point calibration, suspend the probe in known calibration solution. Leave the probe suspended in the solution until readings stabilize. Enter cal,one,y (where y is the known value of the standard) in the command line and hit enter. Only do
this if you do not have two calibration standards.
16. After calibration is complete, upload the OpenCTD software to the Adalogger
M0.

If you do not have access to a system that allows you to maintain a temperature at a stable 25oC, there are two alternatives for calibration. You can use the temperature compensation feature of the Atlas EZO-EC conductivity circuit to set a different stable temperature for calibration, provided that the environment around the probe is stable at that temperature. You can derive the compensation temperature from the OpenCTDs temperature probes, rounded to the nearest tenth of a oC. Set the compensation temperature on the EZO-EC by sending the command t,x through the serial monitor, where x is the compensation temperature rounded to the nearest tenth of a oC. Once temperature compensation is entered, continue through the above two-point calibration protocol. Temperature compensation will reset to 25oC whenever the unit is powered down.

Review the Atlas EZO-EC Datasheet (https://atlas-scientific.com/files/EC_EZO_Datasheet.pdf) for more thorough instructions.

If you cannot maintain a consistent thermal environment, there is one alternative that will result in a rough calibration of the probe acceptable for educational programming or for applications where precise salinity measurements are not essential. On the side of bottles of conductivity solution provided by Atlas Scientific and others, there is usually a table of compensation values in intervals of 5oC. You can calibrate against the value closest to ambient temperature. This method should only be used when there are no alternatives.

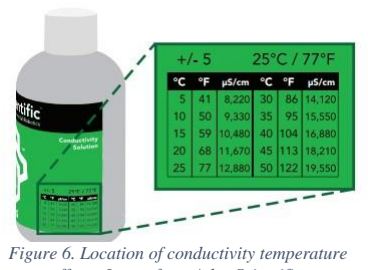
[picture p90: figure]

Conductivity should not need to be calibrated again once the calibration protocol is complete, however it is practice to check calibration at least once per year or whenever components are changed. For more detailed explanation of the calibration process and for an explanation of

Figure 6. Location of conductivity temperature
offsets. Image from Atlas Scientific.

temperature compensation, refer to the Atlas EZO-EC Datasheet (https://atlas-scientific.com/files/EC_EZO_Datasheet.pdf). (https://atlas-scientific.com/files/EC_EZO_Datasheet.pdf)

Each control unit is calibrated to a specific sensor package. Control units are not interchangeable between OpenCTDs without recalibration.

## 4 Data Management

The OpenCTD outputs data as a comma delimited text file which can be read by any standard spreadsheet program. It outputs the date and time followed by pressure in mbar, each of three individual temperatures in oC, and conductivity in µS/cm. In order to convert those values into human-readable oceanographic data, we have produced Microsoft Excel and Google Sheets templates that take the raw data and outputs depth in meters, average temperature, and practical salinity units and generates a basic water column profile.

The template will also average readings in batches of 60 to simplify data presentation. It has fields for calibration constants so that users can input the absolute pressure at sea level at the time of deployment and the temperature offset of the OpenCTD temperature probes determined experimentally during the calibration process.

Although the SD card reader is built into the Adalogger, Arduino M0 microcontrollers do not provide data passthrough. This means that the SD card cannot be read directly from the Adalogger. Data is accessed post-deployment by removing the SD card from the Control Unit and connecting it directly to a computer.

Importing into Excel or Sheets: Open the Excel or Sheets template and navigate to the Data Input sheet in the lower left corner. You can copy-paste the desired data points directly into this sheet.

Data clean-up: Depending on when you started and stopped the OpenCTD, you may have dozens to thousands of rows of data from the surface that you don’t need. Using the reading from the pressure sensor and conductivity probe, remove any date that appears to be from the surface (pressure readings around 1010 and conductivity readings at or near 0).

Water column profile: Select the data that you want to analyze and copy/paste it into the “Paste RAW data from OpenCTD” columns on the Calculations sheet. The water column profile graph should update but you will have to edit the source data fields in order to cover all of your data. You can save the water column profile as an image to embed in presentations or download the cleaned and processed data for more analysis. For long deployments, the final columns average the data over 1-minute intervals.

## 5 Additional Resources

Works Cited

Fofonoff, N.P., Millard Jr, R.C., 1983. Algorithms for the computation of fundamental properties of seawater. UNESCO Tech. Pap. Mar. Sci. 44. https://doi.org/10.25607/OBP-1450 Lewis, E., 1980. The practical salinity scale 1978 and its antecedents. IEEE J. Ocean. Eng. 5, 3–
8. https://doi.org/10.1109/JOE.1980.1145448

Tools and Materials

- Atlas Scientific Conductivity Calibration Solution:
- https://atlas-scientific.com/calibration-solutions/conductivity-calibration-k-1-0-set/ (https://atlas-scientific.com/calibration-solutions/conductivity-calibration-k-1-0-set/)
- Probe Storage Bottle:
- https://amzn.to/43DcMcq

Sensor Specifications

- MS5803-14BA Miniature 14 bar Module:
- https://cdn.sparkfun.com/datasheets/Sensors/Weather/ms5803_14ba.pdf
- DS18B20 1-Wire Digital Thermometer:
- https://datasheets.maximintegrated.com/en/ds/DS18B20.pdf
- EZO-EC Conductivity Circuit Datasheet:
- https://www.atlas-scientific.com/_files/_datasheets/_circuit/EC_EZO_Datasheet.pdf (https://www.atlas-scientific.com/_files/_datasheets/_circuit/EC_EZO_Datasheet.pdf)
- EC K 1.0 Conductivity Probe Datasheet:
- https://files.atlas-scientific.com/Mini_EC_K_1.0_probe.pdf

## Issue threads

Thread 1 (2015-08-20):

### ISSUE TITLE
Dependency List

### ISSUE THREAD

**Issue by Vhati** [OceanographyforEveryone/OpenCTD#1]
I've only ever dabbled in C, so I'm not sure how folks manage dependency hell.

I think I can safely recommend editing the readme to list your reqs.  : )
.
.
Some cursory googling turned up these links...
.
I2C library for the MS5803_14BA 14bar pressure sensor
https://github.com/millerlp/MS5803_14

Dallas Temperature Control for the DS18B20 thermometer
https://milesburton.com/Dallas_Temperature_Control_Library

OneWire **
http://www.pjrc.com/teensy/td_libs_OneWire.html
http://playground.arduino.cc/Learning/OneWire

SD *
https://www.arduino.cc/en/Reference/SD

SoftwareSerial *
http://www.pjrc.com/teensy/td_libs_SoftwareSerial.html
https://www.arduino.cc/en/Reference/SoftwareSerial

SPI **
https://www.pjrc.com/teensy/td_libs_SPI.html
https://www.arduino.cc/en/Reference/SPI

Wire *
http://www.pjrc.com/teensy/td_libs_Wire.html
https://www.arduino.cc/en/Reference/Wire

\* Included with Arduino.
*\* Included with Arduino. A newer version may be available.

(I backslashed the footnote asterisks, so they wouldn't turn into bullet lists)

**Comment by DrAndrewThaler** [comment]
Thank you!

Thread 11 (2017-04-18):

OceanographyforEveryone/OpenCTD #11: Qduino mini board manager

camullen86, 2017-04-18:
When preparing a sketch using the qduino mini i noticed the IDE does not have drivers for this board and found info online suggesting it can easily be bricked if using the wrong setup. i was able to find the board manager and set it up easily enough but a note reminding makers to be aware of this may be good.

i used the following site to get mine set as it has full directions.
https://www.hackster.io/team-qtechknow/qduino-mini-quickstart-guide-8b2d68

SouthernFriedScientist, 2017-04-18:
Thank you! I added the Qtechknow quickstart guide to the README.

closed 2017-04-18 by SouthernFriedScientist

camullen86, 2017-04-23:
Hi Andrew,
i was wondering if you had any issues getting the Qduino Mini to work with
the IDE. I've gone through the full setup to install the board manager and
drivers, everything is up to date. When i launch the IDE it shows Qduino
Mini on COM PORT2 in the bottom right of the application, and is also
selected as the board being used, the problem I'm having is that the Ports
menu is grayed out and inaccessible, and if i try to compile and upload
anything it says it cant reach the board.

there appears to be a hardware issue that says the device needs further
installation, but the drivers and files are all up to date.
So far I haven't been able to find anything useful in any of the forums
about this subject.

Thanks for any insight you may have,
Chris

SouthernFriedScientist, 2017-05-09:
Hi Chris,

If the comm ports don't show up, that generally means there's a driver issue. Have you tried installing all the default Arduino drivers, not just the Qduino specific ones?

If that doesn't work, try pinging https://twitter.com/Qtechknow, they are super helpful and responsive.

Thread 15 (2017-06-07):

OceanographyforEveryone/OpenCTD #15: Inquiry about Arduino UNO with CTD

hpollek, 2017-06-07:
Hello, I am pretty new to Arduino and am trying to build the open CTD 
I was wondering if anyone had suggestions for a pinout guide for use with the Arduino UNO to avoid the failed conductivity readings mentioned with the use of the given pinout on the UNO
Thanks

CTDizzle, 2017-06-07:
hpollek,

I managed to get my first version of the OpenCTD running on the Uno, but
unfortunately I can't seem to find the old code.
I do recall that I was able to get it to read the conductivity, but with
some gibberish. (Now that I think about it, that was probably my fault and
not a function of the UNO)

I think it is definitely possible to get it to work reliably on the UNO.
Atlas-Scientific actually used it when they wrote their sample code
<https://www.atlas-scientific.com/_files/code/Arduino-Uno-EC-sample-code.pdf>.
Try running through their example using the pinouts they use. I think they
define (rx,tx) as (2,3). Once you get that working, you can redefine those
pinouts to suit your needs.

One thing that Atlas-Scientific mentions in their datasheet is to try to
look at the readings while the probe is in solution. If you are getting bad
data in open air, try placing the probe in a cup of tap water. If your data
then looks reasonable, then you can assume that your probe is creating some
interference. Here is the EC EZO datasheet
<https://www.atlas-scientific.com/_files/_datasheets/_circuit/EC_EZO_Datasheet.pdf>.
Page 12 will give you a better description.

Please let me know if you need anymore help. I am still an Arduino amateur
and I could use the practice explaining how things work.

Cheers,
- Ian

-- 
*Ian Black*
M.S. Candidate, Marine Resource Management
Ocean Observatories Initiative (OOI) Technician
College of Earth, Ocean, and Atmospheric Sciences
Oregon State University
Office: 312 Strand Agriculture Hall
Cell: (541) 817-3687

*Interested in OSU's involvement with the OOI?*
Information about the Endurance Array
<http://oceanobservatories.org/array/coastal-endurance/>
Information about Global Station Papa
<http://oceanobservatories.org/array/global-station-papa/>

*More Interesting Things*
Live Feed at Axial Seamount
<http://oceanobservatories.org/streaming-underwater-video/>

hpollek, 2017-06-07:
Thanks a bunch, I got the conductivity sensor to work in the serial monitor!
now the only issue is with the SD card, because at the top of the serial monitor window it says card failed.
Any advice on the SD card pinouts would also be greatly appreciated

CTDizzle, 2017-06-08:
What brand and type of SD card module are you using?

If you are using something similar to what is used in the guide, you'll want to connect the SCK, MOSI, and MISO pins to the same defined pins on the UNO. 

I think those pins are:

SCK - Pin 13
MOSI - Pin 11
MISO - Pin 12
VCC - 3V3
GND - GND

I think the CS pin on the SD module can be connected to any pin you define. The SD library appears to default to pin 10 for CS. If you look at the OpenCTD_qDuino code, you'll notice the lines...

`if (!SD.begin(4))`
`Serial.println("Card failed");  // Log to serial monitor if SD card doesn't work.`

This basically means "if no SD card is detected on pin 4 (the CS), then display "card failed" to the serial monitor." So try connecting your CS to whatever pin you want and place that pin number in those brackets. 

The reference page for [ Serial Peripheral Interface (SPI)](https://www.arduino.cc/en/Reference/SPI) provides a good explanation of the how the protocol works. SPI is the protocol used to communicate with the SD module.

hpollek, 2017-06-08:
Thanks for the help, 
my SD card reader looks like this and is from LC technology
[image]
I have my pins attached as you mentioned with the corresponding number for the CS in the Sketch, but was still getting "card failed" messages and wondering what the number in PinMode() just above the if statement you mentioned should be?

CTDizzle, 2017-06-08:
I see that you have your VCC hooked up to 5v. Try hooking it up to 3.3v.
Make sure it is also hooked up to 3.3v on the UNO.
If that doesn't work, also try changing the SD.begin(10)

I think I have a similar SD card module at home. Let me try a similar set
up and I will try to get back to you in a few hours if I get some
reasonable results.

-- 
*Ian Black*
M.S. Candidate, Marine Resource Management
Ocean Observatories Initiative (OOI) Technician
College of Earth, Ocean, and Atmospheric Sciences
Oregon State University
Office: 312 Strand Agriculture Hall
Cell: (541) 817-3687

*Interested in OSU's involvement with the OOI?*
Information about the Endurance Array
<http://oceanobservatories.org/array/coastal-endurance/>
Information about Global Station Papa
<http://oceanobservatories.org/array/global-station-papa/>

*More Interesting Things*
Live Feed at Axial Seamount
<http://oceanobservatories.org/streaming-underwater-video/>

CTDizzle, 2017-06-09:
I hooked up an old UNO to a DS18B20 temperature sensor and an SD card module. The code I used is below. You can actually exclude the pinMode line.

 You may also try to format your SD card if you haven't already.
- Plug your SD card into your laptop.
- In Windows Explorer, right click on the SD card. Select Format.
- Under File System, select FAT.
- Select Start. 

Pinouts used for the SD Module to UNO.
- GND to GND
- 3.3v to 3.3v
- CS to 4
- MOSI to 11
- SCK to 13
- MISO to 12
Don't hook the 5v to anything. 

If you run the code below (with just your temperature sensor hooked up), you should see the temperature reported to the serial monitor every second. Keep in mind that I only used one temperature sensor, so you may need to adapt the code below to work for you. Then once you pull the SD card, you should see a file named "datalog.txt" that contains the same temperatures you saw in the serial monitor.

`#include <Wire.h>   //Native in Arduino IDE.              
#include <OneWire.h> //Third party library.
#include <DallasTemperature.h>  //Third party library.
#include <SPI.h>   //Native in Arduino IDE.              
#include <SD.h>    //Native in Arduino IDE.              

float temp;   //Make the temperature value a floating point number.
OneWire oneWire(6);   //Data line on temperature sensor goes to pin 6 of arduino.
DallasTemperature tempsensor(&oneWire); //Call DallasTemperature function to "tempsensor"

void setup() {  //Start your engines.
  Serial.begin(9600);   //Set the baud rate to 9600 bps.
  if (SD.begin(4)){   //If an SD card IS detected (with CS to pin 4).
    tempsensor.begin();   //Initialize the temperature sensor.
    delay (500);    //Wait half a second.
  }
  else{
    Serial.println("No card detected. Check to see if card is properly installed."); //If no card is detected, print this message.
    delay(10);  //Wait 10 milliseconds.
    return;
  }
  delay(500);   //Wait half a second.
}

void loop() { //And around we go.
  tempsensor.requestTemperatures(); //Request the temperature from the DS18B20.
  temp =tempsensor.getTempCByIndex(0);  //Define "temp" as the degC value from the probe.
  
  File dataFile = SD.open("datalog.txt", FILE_WRITE); //Create or open a file on the SD card titled "datalog.txt".
  if (dataFile) {   //If dataFile is available,
    dataFile.println(temp); //Print the temperature to it.
    dataFile.close();   //Close the file.

    Serial.println(temp); //Then print that temperature to the serial monitor if the file opened.
  }
  delay(1000);  //Repeat the loop every second.
}`

SouthernFriedScientist, 2017-06-12:
Just wanted to jump in to say that we've found about 5% of those SD card reader/writers are defective out of the package (it's always hard to tell who really makes them because the suppliers/branding change alot, even though they tend to be made by the same factory), so it might also be worth testing the SD reader alone with a known piece of code just to make sure it's not the hardware.

closed 2019-05-20 by SouthernFriedScientist

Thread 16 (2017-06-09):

OceanographyforEveryone/OpenCTD #16: Any way to make the CTD compatible with M0 Pro?

hpollek, 2017-06-09:
Hello, after getting the CTD working fully on my UNO I now have yet another question regarding making the Open CTD work with another board, and this one is giving me more grief.

I'm aiming to potentially get better resolution on the readings by adapting the CTD to be used with the M0 Pro, I have all of the hardware working on the UNO, so now where I've hit this speed bump is with the Sketch, and more specifically, the SoftwareSerial library.

The M0 Pro board does not have SoftwareSerial as a built-in library, as far as I have found online thus far, it is only usable with other Serial functions. I am not very experienced in the wide range of different Arduino board but figured this may be a relatively obvious work-around for someone with more experience and I would appreciate any help that I can get.

Is there any way of achieving the same results as SoftwareSerial with a different approach that would work on this board?
Thanks!

CTDizzle, 2017-06-10:
hpollek,

I have run into the same issue when trying to use the Arduino MKRZero. I
think there is a work around using SamdSercom (
https://www.arduino.cc/en/Tutorial/SamdSercom). You might be able to find a
solution if you look into that and code samples you find around the
internet.
I also haven't tried it out, but maybe you could set the EC EZO to I2C mode
to bypass the need for a Rx/Tx and SoftwareSerial? Atlas-Scientific offers
a tutorial and some sample code for that.

I haven't had the time to really sit down and work out a solution. I have a
research cruise in July that will give me a few days of downtime, so maybe
I will work on it then.

If you do come up with a solution, please let me know because I would
really like to start using the MKR board series for the CTD.

Cheers,
- Ian

<https://github.com/OceanographyforEveryone/OpenCTD/issues/16>, or mute the
thread

CTDizzle, 2017-06-30:
Any luck finding a solution?

hpollek, 2017-06-30:
Initially the Sketch wouldn't even upload to the m0 pro
Now the Sketch is to the point that it compiles and uploads, but the serial monitor shows no readings

CTDizzle, 2017-06-30:
Mind if I take a look at your sketch? You can post it here or email it to blackia@oregonstate.edu
- Ian

SouthernFriedScientist, 2019-05-20:
Hey folks, coming back late to this, but we now have a SoftwareSerial library that will work with M0 boards. You can find it here: https://github.com/OceanographyforEveryone/OpenCTD/tree/master/OpenCTD_Feather_Adalogger/Support_Code/SoftwareSerial

closed 2019-05-20 by SouthernFriedScientist

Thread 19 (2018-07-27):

### ISSUE TITLE
How is the recommended SOIC to DIP adapter used in this project?

### ISSUE THREAD

**Issue by Jake-DeCicco** [OceanographyforEveryone/OpenCTD#19]
For a novice electronics enthusiast like myself, these building instructions are helpful, but I cannot figure out how this adapter should be used or if it even needs to be used at all. As with many concepts I've learned recently, I tried to find information on the internet but I came up short on the entire concept of switching between SOIC and DIP.

**Comment by IanTBlack** [comment]
Hi Jake,

I believe it is used if you decide to piece together the pressure sensor
yourself.

If you opted to use a premade one from SparkFun or Blue Robotics then you
won't need it.

Let me know if you have any other questions or need additional help.

Cheers,
- Ian

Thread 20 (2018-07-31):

OceanographyforEveryone/OpenCTD #20: MS5803 Pressure sensor; Software issue

Jake-DeCicco, 2018-07-31:
**Essentially, the sensor reports data to the serial monitor when I upload the following code (sorry about the formatting):**

#include <Wire.h>
#include <SparkFun_MS5803_I2C.h>

//  ADDRESS_HIGH = 0x76
//  ADDRESS_LOW  = 0x77

MS5803 sensor(ADDRESS_HIGH);

float temperature_c, temperature_f;
double pressure_abs, pressure_relative, altitude_delta, pressure_baseline;

double base_altitude = 1655.0; // Altitude of SparkFun's HQ in Boulder, CO. in (m)

void setup() {
    Serial.begin(9600);
    sensor.reset();
    sensor.begin();
}

void loop() {
  
  temperature_c = sensor.getTemperature(CELSIUS, ADC_512);

  pressure_baseline = sensor.getPressure(ADC_4096);

  temperature_f = sensor.getTemperature(FAHRENHEIT, ADC_512);
  
  pressure_abs = sensor.getPressure(ADC_4096);

  pressure_relative = sealevel(pressure_abs, base_altitude);

  altitude_delta = altitude(pressure_abs , pressure_baseline);
  
  // Report values via UART
  Serial.print("Temperature C = ");
  Serial.println(temperature_c);
  
  Serial.print("Temperature F = ");
  Serial.println(temperature_f);
  
  Serial.print("Pressure abs (mbar)= ");
  Serial.println(pressure_abs);
   
  Serial.print("Pressure relative (mbar)= ");
  Serial.println(pressure_relative); 
  
  Serial.print("Altitude change (m) = ");
  Serial.println(altitude_delta); 

  delay(1000);

  }
  
 double sealevel(double P, double A)
// Given a pressure P (mbar) taken at a specific altitude (meters),
// return the equivalent pressure (mbar) at sea level.
// This produces pressure readings that can be used for weather measurements.
{
	return(P/pow(1-(A/44330.0),5.255));
}

double altitude(double P, double P0)
// Given a pressure measurement P (mbar) and the pressure at a baseline P0 (mbar),
// return altitude (meters) above baseline.
{
	return(44330.0*(1-pow(P/P0,1/5.255)));
}
  

**But fails to do so when I upload code for the entire function of the CTD, even when I eliminate the other sensors from the active code.**

#include <Wire.h>               
#include <SparkFun_MS5803_I2C.h>
#include <MS5803_14.h>
#include <SoftwareSerial.h>
#include <OneWire.h>        
#include <DallasTemperature.h>
#include <SPI.h>               
#include <SD.h>                

float tempA;
float tempB;
float tempC;

float tempAvg;

float EC_float = 0;  // Electrical conductivity.

char EC_data[48];    // A 48 byte character array to hold incoming data from the conductivity circuit. 
char *EC;            // Character pointer for string parsing.

byte received_from_sensor = 0;  // How many characters have been received.
byte string_received = 0;       // Whether it received a string from the EC circuit.

SoftwareSerial ecSerial(8, 9);      // Define the SoftwareSerial port for conductivity.
OneWire oneWire(6);        // Define the OneWire port for temperature.
DallasTemperature sensors(&oneWire);  // Define DallasTemperature input based on OneWire.
MS5803 sensor(ADDRESS_HIGH); //Define pressure sensor

float temperature_c, temperature_f;
double pressure_abs, pressure_relative, altitude_delta, pressure_baseline;
double base_altitude = 1655.0;

void setup(void) {

  Serial.begin(9600);
  ecSerial.begin(9600); 

  pinMode(16, OUTPUT);  // Set data output pin for the SD card reader.
  
  if (!SD.begin(4)) {
    Serial.println("Card failed");
    return; 
  }
  delay(500);

  sensor.reset();
  sensor.begin(); 
  sensors.begin();  
  
  delay(250); 

}

void loop(void) {
  /*if (ecSerial.available() > 0) {
    received_from_sensor = ecSerial.readBytesUntil(13, EC_data, 48);

    // Null terminate the data by setting the value after the final character to 0.
    EC_data[received_from_sensor] = 0;
  }

  // Parse data, if EC_data begins with a digit, not a letter (testing ASCII values).
  if ((EC_data[0] >= 48) && (EC_data[0] <=57)) {
    parse_data();
  }
  delay(10);*/

  temperature_c = sensor.getTemperature(CELSIUS, ADC_512);
  temperature_f = sensor.getTemperature(FAHRENHEIT, ADC_512);
  pressure_abs = sensor.getPressure(ADC_4096);
  pressure_baseline = sensor.getPressure(ADC_4096);
  altitude_delta = altitude(pressure_abs , pressure_baseline);
  
  /*sensors.requestTemperatures();
  tempA = sensors.getTempCByIndex(0);
  tempB = sensors.getTempCByIndex(1);
  tempC = sensors.getTempCByIndex(2);
  tempAvg = (tempA + tempB + tempC) / 3;*/

  logData();  
  sendToSerialMonitor();
  delay(50);
}

void parse_data() {
  EC = strtok(EC_data, ",");                  
}

void logData() {
  /*File dataFile = SD.open("datalog.txt", FILE_WRITE);
  if (dataFile) {
    dataFile.print("Temperature C = ");
    dataFile.println(temperature_c);
    dataFile.print("Temperature F = ");
    dataFile.println(temperature_f);
    dataFile.print("Pressure abs (mbar)= ");
    dataFile.println(pressure_abs);
    dataFile.print("Pressure relative (mbar)= ");
    dataFile.println(pressure_relative); 
    dataFile.print("Altitude change (m) = ");
    dataFile.println(altitude_delta);
    dataFile.print("TempA = ");
    dataFile.print(tempA);
    dataFile.print("  TempB = ");
    dataFile.print(tempB);
    dataFile.print("  TempC = ");
    dataFile.print(tempC);
    dataFile.println("  ");
    dataFile.print("EC = ");
    dataFile.print(EC);
    dataFile.close();
 }
  else {

 }*/
}

void sendToSerialMonitor() {
  Serial.print("Temperature C = ");
  Serial.println(temperature_c);
  
  Serial.print("Temperature F = ");
  Serial.println(temperature_f);
  
  Serial.print("Pressure abs (mbar)= ");
  Serial.println(pressure_abs);
   
  Serial.print("Pressure relative (mbar)= ");
  Serial.println(pressure_relative); 
  
  Serial.print("Altitude change (m) = ");
  Serial.println(altitude_delta);
  
  /*Serial.print("tempA = ");
  Serial.print(tempA);
  Serial.print("  tempB = ");
  Serial.print(tempB);
  Serial.print("  tempC = ");
  Serial.print(tempC);
  Serial.print("  Avg = ");
  Serial.print(tempAvg);
  Serial.println("  ");
  
  Serial.print(EC);
  Serial.println("");*/
}

double altitude(double P, double P0){
// Given a pressure measurement P (mbar) and the pressure at a baseline P0 (mbar),
// return altitude (meters) above baseline.
  return(44330.0*(1-pow(P/P0,1/5.255)));
}
**And btw, thanks for answering my other question in such a timely manner.**

CTDizzle, 2018-07-31:
Hi Jake,

Would you mind emailing me your complete sketch for the CTD and the
hardware that you are using? I have some old CTD parts lying around and I
will take a look during lunch today.

You can send it to blackia@oregonstate.edu.

Thanks,
Ian Black

Squidman32, 2019-06-12:
Did this get resolved?  I'm having a similar issue.  bread boarded everything, and it all worked great.  Potted the depth sensor and data only comes in as 0.00.  So I assumed I screwed it up when I potted it.  I ordered two new depth sensors, when  I bread board both out, all I get is 0.00 coming in.  I cut and pasted your current code (as of 6/12/19) and it still reads 0.00  all the other temp and conductivity work no problem.  any ideas?

SouthernFriedScientist, 2019-06-13:
Good morning, 

Do you have 10K pull up resistors between SCL, SDA, and VCC?

Squidman32, 2019-06-13:
HI Andrew, Thanks so much for the fast response.  I was using the Sparkfun pressure sensor  that didn't require the 10K resistors.  It was working great, I potted it, it stopped working.  At the time I guessed maybe I got epoxy or something somewhere it should go so I tried over again.

I ordered off the shelf pressure sensor set ups like those recommended on the OpenCTD git hub page.  When the new ones came, I bread boarded one to the Qduino and still got 0.00 for readings.  So just to double check, I tried a second sensor, same result. Then I figured maybe the Qduino had a problem, so I swapped it out and solder one of the new pressure sensors to it, and still 0.00.  I'm running 3.3 volts from the VCC on the Qduino.  I tried switching around the SDL and SDA, still 0.00.  I tried loading the pressure sensor testing sketch, same readings.  I cut and pasted all the code straight from the git hub page incase I had a bug in my sketch some where, same result.  The temp and conductivity works no problem, so I'm running out of ideas. It is the weirdest thing as it all worked at one point.  
[image]
[image]
[image]
[image]

SouthernFriedScientist, 2019-06-13:
That is weird. The pressure sensor should be totally fine. Even if you got epoxy on it, it should still read something. I haven't played witht he qDuino code in a while now, but I seem to remember some pressure breakout boards needed the SD card reader to engage before they started reading. Have you tried connecting up everything? From those pictures, it doesn't look like there's anything on the hardware side that should cause it to fail. 

Are you using the qDuino code of the M0 code? You should still be using the qDUino code.

Squidman32, 2019-06-13:
Andrew you are a genius!!!!!  That was it. I hooked up the SD card reader and I'm back in business! The original one had a wire disconnect on the SD reader when I squeezed it in the tube after potting, and that caused the issue.  Thank you so much for your help!

SouthernFriedScientist, 2019-06-14:
Thanks! Though I wouldn't sing my praises too much, after all, I'm the one who wrote the janky code in the first place.

closed 2019-06-14 by SouthernFriedScientist

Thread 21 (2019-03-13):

OceanographyforEveryone/OpenCTD #21: Calibrate Conductivity probe

Squidman32, 2019-03-13:
Under 6.3 conductivity the link " have created a small program for accessing the serial monitor" is dead.  I assumed it was the "simple_serial_for_EC_calibration" in the support code folder.  But when I flashed that over, I only got a stream of 0.00, and got no repsonse when I entered c,0 or k,? or any of the other commands into the serial monitor send command.  Any suggestions?

IanTBlack, 2019-03-13:
Hello,

What microcontroller are you using?  And what conductivity probe are you
using?
I believe you are correct for the support code folder.

My first thought is that you should make sure that your baud is set
correctly for your serial monitor. Another thing to check is to see if you
have the correct line ending selected.
Another thing to check is if you have correctly assigned your RX and TX in
your sketch to what matches for your board.

If you are using the Qduino and talking to the EC EZO via Serial, this is
the code that I used.
https://github.com/IanTBlack/CTDizzle/blob/master/Legacy/Mk3/Qduino_EC_Cal.ino
Give this a shot. If it doesn't work, let me know.

If you are talking to the EC EZO via I2C, you can try modifying this code
to work for your setup:
https://github.com/IanTBlack/CTDizzle/blob/master/Mk5/IDE_EC_Cal.ino

Feel free to get in touch if you have any more questions or issues.
Cheers,
-------------
Ian Black
Faculty Research Assistant | Ocean Observing Center
College of Earth, Ocean, and Atmospheric Sciences | Oregon State University
Cell: (541) 817-3687

IanTBlack, 2019-03-13:
Hello,

What microcontroller are you using?  And what conductivity probe are you
using?
I believe you are correct for the support code folder.

My first thought is that you should make sure that your baud is set
correctly for your serial monitor. Another thing to check is to see if you
have the correct line ending selected.
Another thing to check is if you have correctly assigned your RX and TX in
your sketch to what matches for your board.

If you are using the Qduino and talking to the EC EZO via Serial, this is
the code that I used.
https://github.com/IanTBlack/CTDizzle/blob/master/Legacy/Mk3/Qduino_EC_Cal.ino
Give this a shot. If it doesn't work, let me know.

If you are talking to the EC EZO via I2C, you can try modifying this code
to work for your setup:
https://github.com/IanTBlack/CTDizzle/blob/master/Mk5/IDE_EC_Cal.ino

Feel free to get in touch if you have any more questions or issues.
Cheers
-------------
Ian Black
Faculty Research Assistant | Ocean Observing Center
College of Earth, Ocean, and Atmospheric Sciences | Oregon State University
Cell: (541) 817-3687

Squidman32, 2019-03-13:
Got it to work!!! thank you.
I should have looked harder at your notes.  I had to type in c,0 a few
times before it responded.  Thanks for your help.

Out of curiosity, have you tried tossing an Oxygen sensor on one of these?
I've been look at Pyro Science's little piccolo 2 and/or
firestingO2-SubPort.  Its a bit over my head as this is literally my first
arduino type project and I'm limping along on other people's code.  But it
sure would make this CTD that much cooler if it could do O2.

Lloyd
Lloyd Trueblood Ph.D.
Associate Professor and Chair
Biology Department

<https://lasierra.edu/>

Lloyd.Trueblood@lasierra.edu
Phone: (951) 785-2 <(951)+785-2105>521
Fax: (951) 785-2100

lasierra.edu  <https://brand.lasierra.edu/email-signatures/#>
4500 Riverwalk Parkway | Riverside, CA 92505

Confidentiality: This e-mail (including any attachments) may contain
confidential, proprietary and privileged information, and unauthorized
disclosure or use is prohibited. If you receive this email in error, please
notify the sender and delete this e-mail from your system.

closed 2019-06-13 by SouthernFriedScientist

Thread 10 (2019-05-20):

### ISSUE TITLE
Sample Breaks

### ISSUE THREAD

**Issue by DrAndrewThaler** [OceanographyforEveryone/OpenCTD#10]
Right now, the OpenCTD begins logging as soon as powered on without recording any break in the data. We need to add a feature that adds a sample number to the beginning of each sample series. For example, the first cast of the day starts with a "SAMPLE 1" line in datalog.txt. If the user then power cycles the device, the next time it starts recording is writes a "SAMPLE 2" line in datalog.txt where the new data begins. 

Does this make sense? Are there more elegant solutions?

**Comment by IanTBlack** [comment]
There is an logger demo by Adafruit that will create a newly labeled file every time the device is power cycled.

https://github.com/adafruit/Light-and-Temp-logger/blob/master/lighttemplogger.ino

I'll create a new pull request with my code that implements this.

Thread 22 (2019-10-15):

OceanographyforEveryone/OpenCTD #22: SoftwareSerial

Squidman32, 2019-10-15:
HI Guys, I'm having a library problem, and I'm sure the answer is obvious, but I"m still in the early stages of the github/arduino learning curve.  I can't find the downloadable ZIP file of the modified SoftwareSerial library for the Adafruit feather CTD.  I can navigate to the code on the GitHub page and see it.  But only option I have is to try and cut and paste it, there is no zip/download.  Where can I find the downloadable zip to add the library  to Arduino IDE?

IanTBlack, 2019-10-15:
Are you using the Feather 32u4 or Feather M0? If using the M0, you don't
need SoftwareSerial.
If you want me to give me your components specs, I might be able to fire up
some old code and give you a solution.

Cheers,
-------------
Ian Black
Faculty Research Assistant | Ocean Observing Center
College of Earth, Ocean, and Atmospheric Sciences | Oregon State University
Cell: (541) 817-3687

SouthernFriedScientist, 2019-10-15:
Hello! GitHub is terrible about making simple downloads easy. To get everything in a nice package you either need to clone the OpenCTD library and then access the local version on your desktop, or download the entire OpenCTD repository: https://github.com/OceanographyforEveryone/OpenCTD and then navigate to the libraries in the unpacked .zip file.

Squidman32, 2019-10-16:
Thanks Andrew, That got it for me.  After I got the whole library I was
able to place the SoftwareSerial in and it compiled.
Lloyd Trueblood Ph.D.
Associate Professor and Chair
Biology Department

<https://lasierra.edu/>

Lloyd.Trueblood@lasierra.edu
Phone: (951) 785-2 <(951)+785-2105>521
Fax: (951) 785-2100

lasierra.edu  <https://brand.lasierra.edu/email-signatures/#>
4500 Riverwalk Parkway | Riverside, CA 92505

Confidentiality: This e-mail (including any attachments) may contain
confidential, proprietary and privileged information, and unauthorized
disclosure or use is prohibited. If you receive this email in error, please
notify the sender and delete this e-mail from your system.

closed 2020-06-23 by SouthernFriedScientist

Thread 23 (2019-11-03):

OceanographyforEveryone/OpenCTD #23: Raspberry pi instead of Arduino/Adalogger

gshubham96, 2019-11-03:
Hey Guys

I have been interested in this project and have been wanting to build one for quite some time now. I was wondering however if anyone has tried substituting Arduino/Adafruit combo with a raspberry pi. If yes, is there any text out there that I can follow?

Please also let me know if this is not the right place to ask this question.

SouthernFriedScientist, 2019-11-03:
Hello!

Definitely the right place to ask. Steve Haan has a Pi-based OpenCTD/Camera/BRUV set up. I don't know where he keeps his code, but you can find him on twitter and ask: https://twitter.com/HaanHouse

IanTBlack, 2019-11-04:
Steve Haan has a working PiCTD.
Here is his GitHub Repo:  https://github.com/haanhouse/pictd

I've used some of his Python code to get a working version of a sensor
system using the WhiteBox Labs Tentacle HAT for the Pi and a few Atlas
Scientific Sensors.
Here is my Repo: https://github.com/IanTBlack/FlowThrough

If you are looking for a compact solution, the PiZero would be perfect.
Let me know if you run into any issues. I'd be happy to dust off a Pi and
help out.

Cheers,
-------------
Ian Black
Faculty Research Assistant | Ocean Observing Center
College of Earth, Ocean, and Atmospheric Sciences | Oregon State University
Cell: (541) 817-3687

gshubham96, 2019-11-06:
Hey @SouthernFriedScientist  and @IanTBlack.
Thanks for the quick replies!

I did find PiCTD on Hackaday.io. I will definitely check out the links you posted before I begin. I am planning to start building one sometime in late-January 2020 so plenty of time to plan everything before that.

@IanTBlack 
I am hoping to implement this on a custom stack. Not sure how that would work out yet but I will definitely update when I have it figured out. :) Finally, I want to deploy one in a lake. Atlas Scientific seem to have most of the sensors I am interested in. Thanks for posting about it.

Appreciate the help. Considering there might be no big updates till January, should I close the issue or keep it open ?

Regards
Shubham Garg

closed 2020-09-25 by SouthernFriedScientist

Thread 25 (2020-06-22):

OceanographyforEveryone/OpenCTD #25: Independent System Not taking values

MattChace, 2020-06-22:
Uploading the code from my computer Arduino IDE and opening the Serial Monitor I am seeing the sensor take values and store them to the SD Card, I remove the SD Card and read the txt file on my computer and confirm that the values were saved. 
However, when the MCU is powered by a battery and I did a test cast, I open the txt file and find it empty. Not sure why the code is not running when it is turned on by the battery. Any assistance would be greatly appreciated!!

IanTBlack, 2020-06-22:
Hi Matt,
Which version of the OpenCTD are you working with? If you have modified you code, can you attach it?

Thanks,
- Ian

MattChace, 2020-06-22:
Hi Ian!!
Thanks for the quick response! We are working with the Version of the CTD that is within the Construction/Operation Manual and followed all the steps within that text, I have attached my Arduino Code below.

Thanks!

  *   Matt

Matthew Chace

Bachelors of Science in Electrical Engineering

Wentworth Institute of Technology

Boston, Massachusetts

IanTBlack, 2020-06-22:
Hi Matt,
Doesn't look like it attached properly. You might have to do it directly through the GitHub website.

Couple more questions.

1) If you add an empty SD card, is the text file created, but remains empty?

2) Is the SD card seated properly?
   -If you operate it under battery on the bench, you could try tying the EC EZO LED to turn on/off if the SD card is not detected. See lines 140-144 here: https://github.com/IanTBlack/CTDizzle/blob/master/Adafruit_M0_Mk5/2019-04-29_Profile.ino

3) What battery are you using?

Unfortunately I don't have an M0 Adalogger, but I do have a BLE M0 Feather + Adalogger featherwing, so I will see if I can recreate your problem once I get your code.

- Ian

MattChace, 2020-06-22:
My Code is pasted below, I put a new micro sd into the board and turned it on. The MCU doesnt create a txt file at all. 

``//Date and time functions using a DS3231 RTC connected via I2C and Wire lib
#include <Wire.h>
#include "RTClib.h"

//serial peripheral interface and library for SD card reader
#include <SPI.h> //serial peripheral interface for SD card reader
#include <SD.h> //library for SD card reader

//communication protocols for temperature sensors
#include <OneWire.h>  
#include <DallasTemperature.h>   

//Software libary for the pressure sensor
#include <MS5803_14.h>

//EC Circuit uses software serial
#include <SoftwareSerial.h>

RTC_DS3231 rtc; //define real-time clock

const int chipSelect = 4; //sets chip select pin for SD card reader

MS_5803 sensor = MS_5803(512); // Define pressure sensor.

OneWire oneWire(6); // Define the OneWire port for temperature.
DallasTemperature sensors(&oneWire); //Define DallasTemperature input based on OneWire.

SoftwareSerial ecSerial(12, 13); // Define the SoftwareSerial port for conductivity.

double pressure_abs; //define absolute pressure variable

//Declare global temperature variables.
float tempA;
float tempB;
float tempC;

//Declare global variables for eletrical conductivity
float EC_float = 0;  
char EC_data[48]; // A 48 byte character array to hold incoming data from the conductivity circuit. 
char *EC; // Character pointer for string parsing.
byte received_from_sensor = 0; // How many characters have been received.
byte string_received = 0; // Whether it received a string from the EC circuit.

void setup () {

// comment the following three lines out for final deployment
  #ifndef ESP8266
    while (!Serial);   //for Leonardo/Micro/Zero
 #endif

  Serial.begin(9600);

//Initialize SD card reader
  Serial.print("Initializing SD card...");

  if (!SD.begin(chipSelect)) {
    
    Serial.println("Card failed, or not present");
    return;
    
  }
  
  Serial.println("card initialized.");

  delay(1000); 

  if (! rtc.begin()) {
    
[... 230 lines cut ...]
    }
  
    dataFile.print("  ");
    dataFile.print(pressure_abs);
    dataFile.print("  ");  
    dataFile.print(tempA);
    dataFile.print("  ");
    dataFile.print(tempB);
    dataFile.print("  ");
    dataFile.print(tempC);
    dataFile.print("  "); 
    dataFile.println(EC);
    dataFile.close();    

  }
  
  delay(50);

}

void parse_data() { // Parses data from the EC Circuit.

  EC = strtok(EC_data, ",");                  

}`

SouthernFriedScientist, 2020-06-23:
Hello,

Lines 48, 49, and 50...  

`  #ifndef ESP8266
    while (!Serial);   //for Leonardo/Micro/Zero
 #endif `

...provide diagnostic information during assembly and should be commented out or removed from the code prior to deployment, otherwise the Arduino will look for a serial connection before writing to the SD card.

MattChace, 2020-06-24:
That worked!! Thank you so much!

Matthew Chace

closed 2020-09-25 by SouthernFriedScientist

goldsphininx, 2020-09-25:
House cleaning. ;)

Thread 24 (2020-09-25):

### ISSUE TITLE
Robust comparison to commercial CTD?

### ISSUE THREAD

**Issue by camrinbraun** [OceanographyforEveryone/OpenCTD#24]
I see the 2 datasets included for comparison but surely there's data out there seeing how these stack up against any of the major CTDs in the coastal ocean? Trying to decide whether to embark on this project which depends on the accuracy and precision in conductivity primarily.

I also saw a comment in another issue on measuring DO. Any progress on that front?

Really cool tool you guys have created. Thanks!

**Comment by IanTBlack** [comment]
Hello,

I think I have some data on a hard drive somewhere with comparisons between
shipboard Sea-Bird CTD rosettes and YSI Castaways. I'll see if I can find
it. There were a few times that I deployed the CTDs to 100m, and after a
couple profiles they flooded (that's a manufacturing oversight on my part),
so repeated data on a single CTD is sparse.

In my build, I used the TSYS01 as the temperature sensor, which has been
great in building confidence in the temperature compensation of
conductivity.
Off the top of my head, there were days when I was able to achieve a 0.2
PSU difference from a vetted CTD, some days I was off by more than 1 PSU.
One source of error is probably in the environment that I calibrated the
Atlas K1.0 probe. I would often calibrate the conductivity probe in my
kitchen, not really considering ambient temperature or attempting repeated
calibrations. I once calibrated one of my open source CTDs in a cold room
and noticed an improvement. I think that was the one that had to 0.2 PSU
difference. If you have access to a temperature controlled lab or
refrigerator, I would recommend performing calibrations that way.

I think noise in the circuit also causes some issues in the accuracy and
precision in the conductivity reading. Atlas-Scientific offers voltage
isolators for their EC EZOs. At the very least, it should make a reading
stable, so then you could hone the accuracy through calibration. You may be
able to find other conductivity probes that work, but when I last looked a
couple of years ago, Atlas-Scientific was the only pressure-capable probe
that was off-the-shelf.

Atlas-Scientific also offers a DO probe. A couple years ago I made a repo
with a sketch on how to get it running on an Arduino.
https://github.com/IanTBlack/OTP
Although I've recently begun to implement the Raspberry Pi in my work, so I
would recommend going that route if you are Python savvy. Whether you go
Arduino or RPi depends on your end use. Each has their own advantages.

If you do decide to build one, let me know. I have some parts that are
collecting dust and could be useful.

Let me know if you have any more questions,
-------------
Ian Black
Faculty Research Assistant | Ocean Observing Center
College of Earth, Ocean, and Atmospheric Sciences | Oregon State University
Cell: (541) 817-3687

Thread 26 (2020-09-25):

### ISSUE TITLE
Adafruit Feather MO Bluefruit LE [ID:2995]

### ISSUE THREAD

**Issue by MattChace** [OceanographyforEveryone/OpenCTD#26]
Not particularly an issue with this current design, but my team is trying to introduce the Bluetooth compatible Adalogger to the design to reduce the amount of times the CTD needs to be opened to access data (We have developed a GUI to display this data as well) and we recognize that the Arduino code needs to be altered to support bluetooth communication over serial/SD Card. A lot of the Adafruit demo code utilizes an app to link to the adalogger but we are aiming for a pc connection. I am looking for assistance with the arduino code for this if anyone has attempted it already or has any insight. As of now we only have the code written on this github page. The link to the bluetooth adalogger is below.
https://www.adafruit.com/product/2995?gclid=EAIaIQobChMIxu7496u56gIVjI7ICh3Sqg5jEAAYASAAEgJat_D_BwE

**Comment by IanTBlack** [comment]
Hi Matt,

The most recent version of the CTDizzle (based off the OpenCTD) uses the
Adafruit M0 Bluefruit.  You could probably cobble something together from
that repo. Note that I have not improved upon this code in some time and it
needs to be cleaned up. https://github.com/IanTBlack/CTDizzle

I have it set up to use the Bluefruit Android App, but there may be example
sketches that will connect to a PC via Bluetooth. I wouldn't be surprised
if there is a Python library that supports BTLE or if Teraterm supports it.

Let me know if you run into any issues.
- Ian

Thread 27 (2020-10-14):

### ISSUE TITLE
Maximum depth of OpenCTD?

### ISSUE THREAD

**Issue by Geoboy2020** [OceanographyforEveryone/OpenCTD#27]
I would like to build an OpenCTD for use on Lake Chelan, max depth 453m (3rd deepest lake in the U.S.). What is the likely max operating depth of the current design? If it is on the order of 200m, are there obvious modifications that could extend its operating depth to 500m? Would a mineral oil fill work for that purpose? 

I have an EXO3 that we deploy for profiles in shallower parts of the lake, but it only goes to 250m max depth. 

The EXO3 will provide a commercial instrument comparison with OpenCTD profiles to 250m depth if we can manage to build one.

Phil Long
Lake Chelan Research Institute 
KeepChelanBlue.org

**Comment by IanTBlack** [comment]
Hi Phil,

I believe Andrew has tested it to ~120m on the newer version. I'll have to
do some research on the pressure sensor, but your max operating range is 14
bar, so you'd have to upgrade to a new pressure sensor. You'd probably also
want to find an alternative to the plug cap.

You could try using a Blue Robotics aluminum case, which is what I have
done in my open source CTD builds.

Alternatively, you could increase the schedule of the PVC and pack on the
epoxy.

I'm travelling across the country right now. I should be able to give you a
more detailed response once I get back home.

Cheers,
- Ian

**Comment by DrAndrewThaler** [comment]
Hello,

We've tested the housing to 150 meters, however, the depth sensor is currently only rated to 14Bar, which works out to about 140 meters (with slight variation depending on water density and altitude). There is a 30 bar module that will get you the 300 meters which I am working on integrating. Source code is still being tested, but I'd be happy to send you the BoM and code to test as long as you understand that it's super provisional and hasn't been field tested yet. 

~Andrew

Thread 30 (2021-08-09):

OceanographyforEveryone/OpenCTD #30: Conductivity calibration

gheleguen, 2021-08-09:
Hi everyone, 

I made an open CTD for an antarctic expedition. This one must leave before 1st September. 
All is ok. I have just a problem with conductivity calibration. 
When I send c,0 or other command. I didn't got any response. 
The response of conductivity sensor in fresh water is around 300. Is it µS/cm ? 

The baud range is ok and TX and RXpin also right.

I work for an other job with teensy 3.6 board. I think Arduino IDE work with it's SoftwareSerial librairies. 

My Hardware is EZO board and mini conductivity probe k1.0. 

Excuse my english level. I'm french.

Best regards

Guillaume Leguen

IanTBlack, 2021-08-09:
> [This email originated from outside of OSU. Use caution with links and attachments.]

Hello Guillaume,

The documentation for the EC EZO can be confusing. It's been a while since I have built a CTD so I just went through it again.

When you send a "c,0", you are telling the EC EZO to stop auto sampling when in UART mode. If you have responses turned off with the "OK,0" command, then you won't get a string "OK" at the end of each response. To turn on responses, enter "OK,1".

Did you try sending a "R" command after turning off auto sampling? That should return a reading. To turn on auto sampling when you are done with the calibration, enter "c,1".

Given the accuracy of the sensor, I would say 300 uS/cm is reasonable for fresh water. Did you try it in distilled water?

Cheers,
- Ian

gheleguen, 2021-08-09:
Hi Ian,

Really thanks for your queekly response. 
It's working. But in the first time it didn't working. I don't know why. 
But my CTD is calibrated. 

It's bizare but it's ok ;-)

Have a good day

Guillaume

IanTBlack, 2021-08-09:
That's great. I'm glad it is working. Sometimes it is as simple as restarting the whole thing!

I am interested to see how you use the CTD in Antarctica.  Keep us updated!

SouthernFriedScientist, 2021-08-10:
Hello,

Glad to hear you got it working. I've also occasionally had issues with the serial connection while calibrating the conductivity probe, but find a reset will get it moving again. The good news is you shouldn't have to calibrate it very often. 

It is  µS/cm. 

Make sure you reenabled autosampling before re-flashing the OpenCTD software (and that you edited out the three lines of diagnostic code that pause the sensors until a serial connection is established). 

All the best and looking forward to seeing what you do in Antarctica!

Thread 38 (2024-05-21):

### ISSUE TITLE
Battery polarity - important note when ordering the Amazon LiPos

### ISSUE THREAD

**Issue by pwnel** [OceanographyforEveryone/OpenCTD#38]
When ordering LiPo batteries from Amazon (using the Amazon link in the construction manual instead of the Adafruit link), be advised that the Amazon LiPos come with the polarity of the JST connector REVERSED.  The [M0 manual ](https://cdn-learn.adafruit.com/downloads/pdf/adafruit-feather-m0-adalogger.pdf )calls this out specifically (red box from manual inserted below) and it's worth adding this warning in the next iteration of the construction manual.  (NOTE: AdaFruit is out of stock of the LiPo batteries at this time, so it's useful to have the Amazon alternative - provided one is aware of the polarity issue)

<img width="1096" alt="Screen Shot 2024-02-14 at 4 10 19 PM" src="https://github.com/OceanographyforEveryone/OpenCTD/assets/9678065/db8e6ea2-0198-485c-9440-db46c3068d3b">

**Comment by DrAndrewThaler** [comment]
Thank you! That is so frustrating.

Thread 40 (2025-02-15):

OceanographyforEveryone/OpenCTD #40: Adafruit Feather M0 Disconnects during OpenCTD_mo.ino Upload?

EllisWebb, 2025-02-15:
Hello, 
Control unit assembled; IDE, Boards, and Libraries downloaded!

Notes: 

- Arduino IDE 2.3.4
- Mac OS Sequoia 15.2
- Carrier Board 7c
- Adafruit Feather RP2040 AdaLogger Flash with microSD Card (Part No 5980) 

**The OpenCTD_mo.ino compiles without issue seemingly. Unfortunately, as soon as the IDE gets to the upload phase the lower right hand corner of the IDE changes from:**

"Adafruit Feather M0 (SAMD21) on /dev/cu.usbmodem1101"

**to:**

"Adafruit Feather M0 (SAMD21) on /dev/cu.usbmodem1101 [not connected]"

**The output window then throws the following error:**

"No device found on cu.usbmodem1101
Failed uploading: uploading error: exit status 1"

I believe I have ensured I am using the right board, "Adafruit Feather M0 (SAMD21)" and connected to the right port /dev/cu.usbmodem1101 initially, however, during the upload phase it somehow causes the AdaLogger to disconnect? 

**Upon online research there may be a few issues I believe I could be encountering.** 

1. Drivers not automatically downloading? 
_I see no indication of 6.7.3 "Connect your Adalogger to your laptop using a micro-USB cable. The
necessary drivers should automatically install." being successfully completed. Though I also don't know where to look for said drivers..._

2. UBS C - USB C chord is charging only? 
_The Adafruit Feather M0 we are working with has a USB C port not micro-USB. Some websites have recommended to purchase specific USB C chord, this is the first I am hearing of this issue, in any capacity, then again I haven't used many USB C - C chords to date._

3. Other recommendations seem to site AdaLogger Reset protocols or Manual Bootloader protocols? 
_Being novice, we are slightly hesitant to take these steps. _

4. Other issues I haven't listed or read about yet?

**Any advice welcome!** 

Thanks, 
Carter & Rich

IanTBlack, 2025-02-15:
Does the board take up a serial port when you connect via IDE?
Are you able to upload an example sketch from Arduino like blink.ino?
If you are not able to do that, my first thought is that your cable may not be a data cable. But if you are able to see the connection appear in your device manager then maybe it is not the cable.

Did you add the Adafruit URL to the additional boards manager? 
https://learn.adafruit.com/adafruit-feather-m0-basic-proto/setup

IanTBlack, 2025-02-15:
@EllisWebb I just looked over your post again and I just realized you are using the Adafruit RP2040 Feather, not an M0.

You should follow this guide to set it up instead. 
https://learn.adafruit.com/adafruit-feather-rp2040-pico/arduino-ide-setup?gad_source=1&gclid=EAIaIQobChMIrenNxOXEiwMV_RitBh0ydzmwEAAYASAAEgIVTvD_BwE

IanTBlack, 2025-02-15:
Even though you do not have an M0, I suspect that you could get things to run on the RP2040 with Arduino. 
Based on the RP2040 Arduino guide I linked above, it looks like the pinouts do not align with what is on the board. You may need to adjust the wiring or the identified pins in the sketch to get things to work for the OpenCTD. Something to keep in mind.

EllisWebb, 2025-02-17:
This makes a lot of sense, simple build list error.  Thanks for the links. 

Will be an exciting to learn how to change the identified pins in the sketch! 

Thanks for the heads up and the advice,
Carter

closed 2025-02-17 by EllisWebb

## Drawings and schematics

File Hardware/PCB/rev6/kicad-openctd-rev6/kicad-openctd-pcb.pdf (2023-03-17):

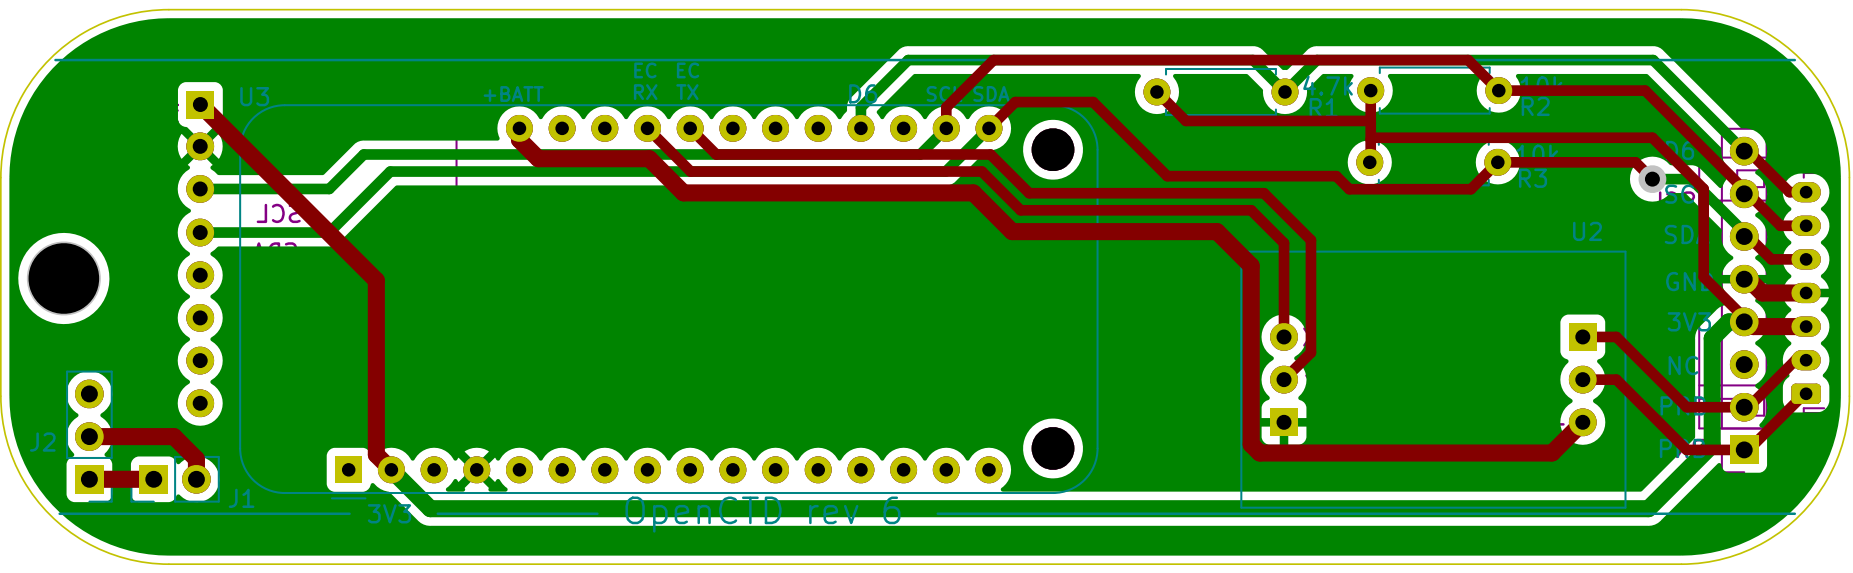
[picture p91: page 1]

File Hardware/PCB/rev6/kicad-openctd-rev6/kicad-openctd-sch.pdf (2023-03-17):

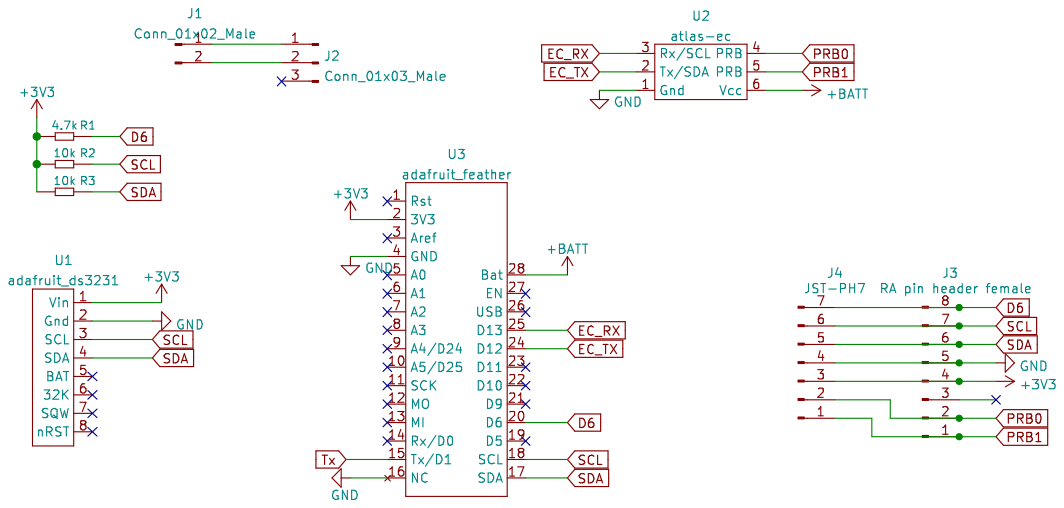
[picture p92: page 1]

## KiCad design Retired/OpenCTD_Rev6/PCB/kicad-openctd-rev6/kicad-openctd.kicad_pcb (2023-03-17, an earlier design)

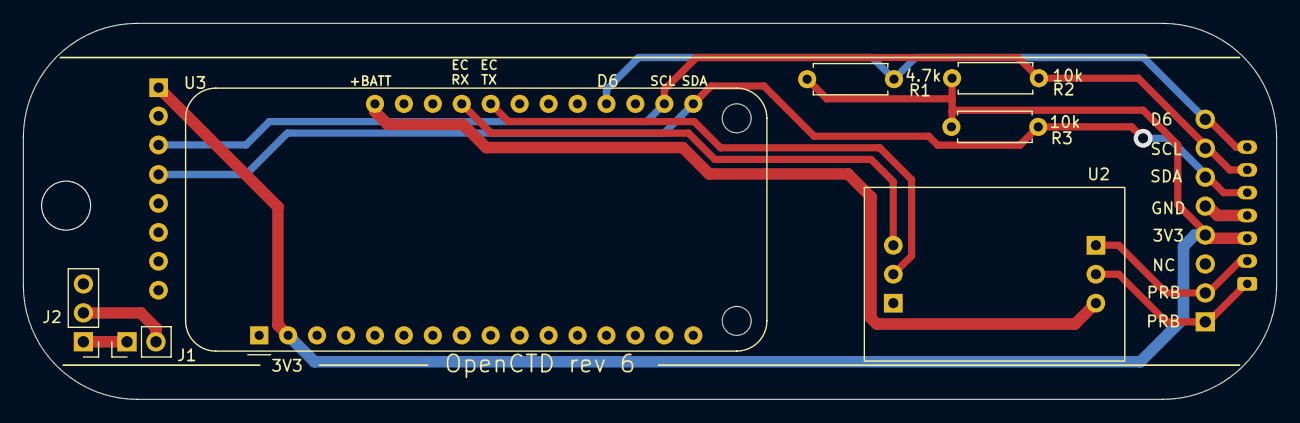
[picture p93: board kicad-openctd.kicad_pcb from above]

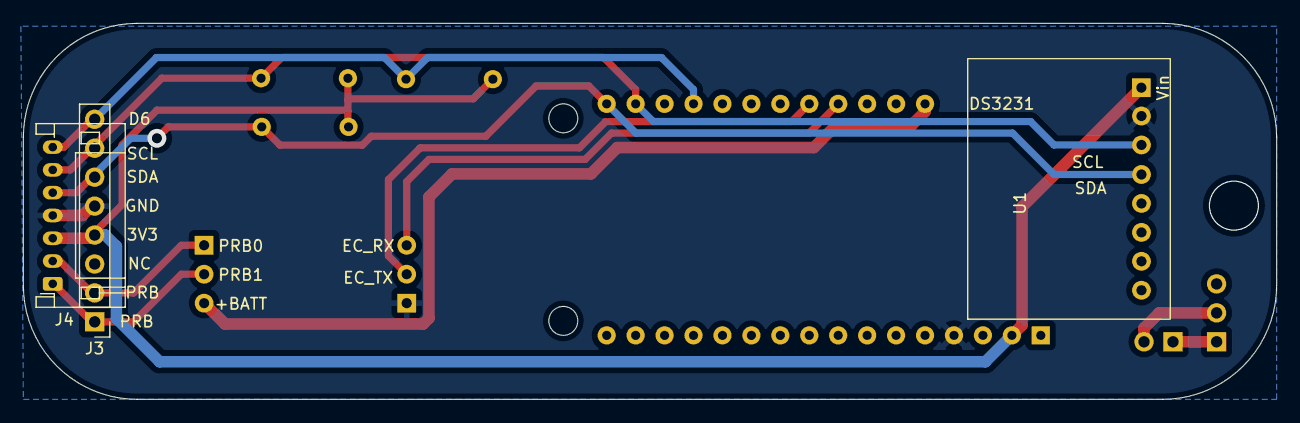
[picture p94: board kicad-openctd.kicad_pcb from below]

Board: 2 copper layers, 110.0 x 33.0 mm, 10 parts (3 on the bottom side), 12 nets.

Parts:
J1: Conn_01x02_Male; PinHeader_1x02_P2.54mm_Vertical
J2: Conn_01x03_Male; PinHeader_1x03_P2.54mm_Vertical
J3: RA pin header female; PinHeader_1x08_P2.54mm_Vertical
J4: JST-PH7; JST_PH_S7B-PH-K_1x07_P2.00mm_Horizontal
R1: 4.7k; R_Axial_DIN0207_L6.3mm_D2.5mm_P7.62mm_Horizontal
R2, R3: 10k; R_Axial_DIN0207_L6.3mm_D2.5mm_P7.62mm_Horizontal
U1: adafruit_ds3231; Adafruit_DS3231_flipped_noholes
U2: atlas-ec; Atlas_EC
U3: adafruit_feather; Adafruit_Feather_With2MountingHoles

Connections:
+3V3: J3.4, J4.3, R1.1, R2.1, R3.1, U1.1 (Vin), U3.2 (3V3)
+BATT: U2.6 (Vcc), U3.28 (Bat)
D6: J3.8, J4.7, R1.2, U3.20 (D6)
EC_RX: U2.3 (Rx/SCL), U3.25 (D13)
EC_TX: U2.2 (Tx/SDA), U3.24 (D12)
GND: J3.5, J4.4, U1.2 (Gnd), U2.1 (Gnd), U3.4 (GND)
unnamed: J1.1, J2.1
unnamed: J1.2, J2.2
PRB0: J3.2, J4.2, U2.4 (PRB)
PRB1: J3.1, J4.1, U2.5 (PRB)
SCL: J3.7, J4.6, R2.2, U1.3 (SCL), U3.18 (SCL)
SDA: J3.6, J4.5, R3.2, U1.4 (SDA), U3.17 (SDA)

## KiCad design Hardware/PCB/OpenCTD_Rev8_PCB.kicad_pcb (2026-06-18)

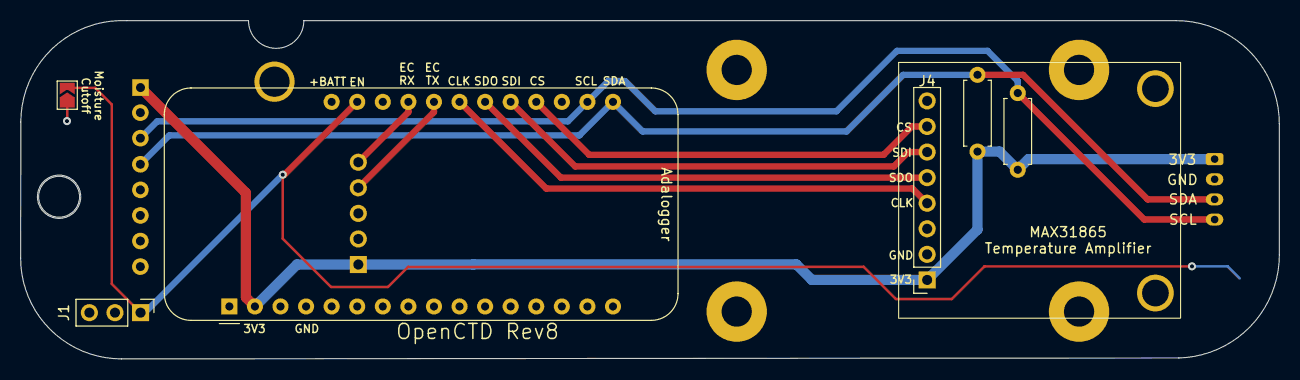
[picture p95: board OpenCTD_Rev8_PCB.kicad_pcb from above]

Board: 2 copper layers, 125.0 x 33.6 mm, 5 parts (1 on the bottom side), 5 nets.

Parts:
J1: Conn_01x03_Male; PinHeader_1x03_P2.54mm_Vertical
R2, R3: 10k; R_Axial_DIN0207_L6.3mm_D2.5mm_P7.62mm_Horizontal
U1: adafruit_ds3231; Adafruit_DS3231_flipped_noholes
U3: adafruit_feather; Adafruit_Feather_With2MountingHoles

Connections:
+3V3: R2.1, R3.1, U1.1 (Vin), U3.2 (3V3)
EN: J1.1, U3.27 (EN)
GND: J1.2, U1.2 (Gnd), U3.4 (GND), U3.16 (NC)
SCL: R2.2, U1.3 (SCL), U3.18 (SCL)
SDA: R3.2, U1.4 (SDA), U3.17 (SDA)

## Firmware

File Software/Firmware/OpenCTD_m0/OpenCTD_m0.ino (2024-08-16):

//Date and time functions using a DS3231 RTC connected via I2C and Wire lib
#include <Wire.h>
#include "RTClib.h"

//serial peripheral interface and library for SD card reader
#include <SPI.h> //serial peripheral interface for SD card reader
#include <SD.h> //library for SD card reader

//communication protocols for temperature sensors
#include <OneWire.h>
#include <DallasTemperature.h>

//Software libary for the pressure sensor
#include <MS5803_14.h>

//EC Circuit uses software serial
#include <SoftwareSerial.h>

RTC_DS3231 rtc; //define real-time clock

const int chipSelect = 4; //sets chip select pin for SD card reader
char datalogFileName[12];

/* This integer specifies how high accuracy you want your pressure sensor to be (oversampling resolution).
   Ok values: 256, 512, 1024, 2048, or 4096 (Higher = more accuracy but slower sampling frequency**)
 * ** There is no reason not to use the highest accuracy. This is because the datalogging rate is set by the
   sampling/response frequency of the ec sensor [default = 1 sec] (this is to avoid the case where both sensors send data at the same time). */

#define PRESSURE_SENSOR_RESOLUTION 4096
MS_5803 sensor = MS_5803(PRESSURE_SENSOR_RESOLUTION); // Define pressure sensor.

OneWire oneWire(6); // Define the OneWire port for temperature.
DallasTemperature sensors(&oneWire); //Define DallasTemperature input based on OneWire.

SoftwareSerial ecSerial(12, 13); // Define the SoftwareSerial port for conductivity.

double pressure_abs; //define absolute pressure variable

/* This integer specifies how high resolution you want your temperature sensors to be.
   Ok values: 9,10,11,12 (Higher = more accuracy but slower sampling frequency**)
 * ** There is no reason not to use the highest accuracy. This is because the datalogging rate is set by the
   sampling/response frequency of the ec sensor [default = 1 second] (this is to avoid the case where both sensors send data at the same time). */

#define TEMP_SENSOR_RESOLUTION 12

//Declare global temperature variables.
float tempA;
float tempB;
float tempC;
int tempADelayStartTime; // Define a variable to mark when we requested a temperature mesurement from A so we can wait the required delay before reading the value.
int tempBDelayStartTime; // Define a variable to mark when we requested a temperature mesurement from B so we can wait the required delay before reading the value.
int tempCDelayStartTime; // Define a variable to mark when we requested a temperature mesurement from C so we can wait the required delay before reading the value.
int requiredMesurementDelay = sensors.millisToWaitForConversion(TEMP_SENSOR_RESOLUTION);

//Declare global variables for eletrical conductivity
float EC_float = 0;
char EC_data[48]; // A 48 byte character array to hold incoming data from the conductivity circuit.
char *EC; // Character pointer for string parsing.
byte received_from_sensor = 0; // How many characters have been received.
byte string_received = 0; // Whether it received a string from the EC circuit.

#define EC_SAMPLING_FREQUENCY 1 // Set the requested sampling frequency of the conductivity probe in seconds (NO Decimals) (this by extension sets the overall frequency of logging).
#define EC_LED 1 // Set the LED on the EZO EC Chip. 1 to turn on, 0 to turn off to preserve power

void setup () {

  // comment the following three lines out for final deployment
//#ifndef ESP8266
// while (!Serial && millis() < 20000); //for Leonardo/Micro/Zero - Wait for a computer to connect via serial or until a 20 second timeout has elapsed (This works because millis() starts counting the mlliseconds since the board turns on)
//#endif

  Serial.begin(9600);

  //Initialize SD card reader
  Serial.print("Initializing SD card...");

  while (!SD.begin(chipSelect)) {

    Serial.println("Card failed, or not present");
    delay(1000);

  }

  // This funny function allows the sd-library to set the correct file created & modified dates for all sd card files.
  // (See the SDCardDateTimeCallback function defined at the end of this file)
  SdFile::dateTimeCallback(SDCardDateTimeCallback);

  Serial.println("card initialized.");

  delay(1000);

  if (! rtc.begin()) {

    Serial.println("Couldn't find RTC");
    while (1);

  }

  get_numbered_filename(datalogFileName, "CAST", "CSV");

  Serial.print("Writing to datalog: ");
  Serial.println(datalogFileName);

  File dataFile = SD.open(datalogFileName, FILE_WRITE);

  if (dataFile) {
    Serial.println("====================================================");
    Serial.println("Date, Time,Pressure,Temp A,Temp B,Temp C,Conductivity");
    dataFile.println("Date, Time,Pressure,Temp A,Temp B,Temp C,Conductivity");
    dataFile.close();

  } else {
    Serial.println("Err: Can't open datalog!");
  }

  //Initialize real-time clock
  if (rtc.lostPower()) {

    //reset RTC with time when code was compiled if RTC loses power
    Serial.println("RTC lost power, lets set the time!");
    rtc.adjust(DateTime(F(__DATE__), F(__TIME__)));

  }

  delay(250);   // Wait a quarter second to continue.

  //Initialize sensors
  Serial.println("-- Pressure Sensor Info: --");
  sensor.initializeMS_5803(); // Initialize pressure sensor
  Serial.println("---------------------------");
  
  sensors.begin();  // Intialize the temperature sensors.
  sensors.setResolution(TEMP_SENSOR_RESOLUTION);  // Set the resolution (accuracy) of the temperature sensors.
  sensors.requestTemperatures(); // on the first pass request all temperatures in a blocking way to start the variables with true data.
  tempA = get_temp_c_by_index(0);
  tempB = get_temp_c_by_index(1);
  tempC = get_temp_c_by_index(2);

  sensors.setWaitForConversion(false);  // Now tell the Dallas Temperature library to not block this script while it's waiting for the temperature mesurement to happen

  ecSerial.begin(9600); // Set baud rate for conductivity circuit.

  do {

    ecSerial.write('i');  // Tell electrical conductivity board to reply with the board information by sending the 'i' character ...
    ecSerial.write('\r'); // ... Finish the command with the charage return character.

    received_from_sensor = ecSerial.readBytesUntil('\r', EC_data, 30); // Wait for the ec circut to send the data before moving on...
    EC_data[received_from_sensor] = 0; // Null terminate the data by setting the value after the final character to 0.

  } while (EC_data[1] != 'I'); // Keep looping until the ecSerial has sent the board info string (also indicating it has booted up, I think...)

  Serial.print("EC Board Info (Format: ?I,[board type],[Firmware Version]) -> "); Serial.println(EC_data);

  delay(10);
  ecSerial.write('C');  // Tell electrical conductivity board to continously ("C") transmit mesurements ...
  ecSerial.write(',');  //
  ecSerial.print(EC_SAMPLING_FREQUENCY);    // ... every x seconds (here x is the EC_SAMPLING_FREQUENCY variable)
  ecSerial.write('\r'); // Finish the command with the carrage return character.
    
  ecSerial.write('L');  // Tell electrical conductivity board to turn off LED to preserve power ...
  ecSerial.write(',');  //
  ecSerial.print(EC_LED);  // 1 to turn light on, 0 to turn light off
  ecSerial.write('\r'); // ... Finish the command with the charage return character.

  received_from_sensor = ecSerial.readBytesUntil('\r', EC_data, 10); // keep reading the reply until the return character is recived (or it gets to be 10 characters long, which shouldn't happen)
  EC_data[received_from_sensor] = 0; // Null terminate the data by setting the value after the final character to 0.
  Serial.print("EC Frequency Set Sucessfully? -> "); Serial.println(EC_data);
  Serial.print("EC LED on or off? -> ");
  if (EC_LED > 0) {Serial.println("on");}
    else {Serial.println("off");}

  Serial.println("--- Starting Datalogging ---");
}

void loop () {

  //Read electrical conductivity sensor
  if (ecSerial.available() > 0) {

    received_from_sensor = ecSerial.readBytesUntil(13, EC_data, 48);
    EC_data[received_from_sensor] = 0; // Null terminate the data by setting the value after the final character to 0.

    if ((EC_data[0] >= 48) && (EC_data[0] <= 57)) { // Parse data, if EC_data begins with a digit, not a letter (testing ASCII values).

      parse_data();

    }

    // Read the temperature sensors.
    if (millis() - tempADelayStartTime > requiredMesurementDelay) { // wait for conversion to happen before attempting to read temp probe A's value;
      tempA = get_temp_c_by_index(0);
      sensors.requestTemperaturesByIndex(0);  // request temp sensor A start mesuring so it can be read on the following loop (if enough time elapses).
      tempADelayStartTime = millis();  // mark when we made the request to make sure we wait long enough before reading it.
    }

    if (millis() - tempBDelayStartTime > requiredMesurementDelay) { // wait for conversion to happen before attempting to read temp probe B's value;
      tempB = get_temp_c_by_index(1);
      sensors.requestTemperaturesByIndex(1);  // request temp sensor B start mesuring so it can be read on the following loop (if enough time elapses).
      tempBDelayStartTime = millis();  // mark when we made the request to make sure we wait long enough before reading it.
    }


    if (millis() - tempCDelayStartTime > requiredMesurementDelay) { // wait for conversion to happen before attempting to read temp probe C's value;
      tempC = get_temp_c_by_index(2);
      sensors.requestTemperaturesByIndex(2);  // request temp sensor C start mesuring so it can be read on the following loop (if enough time elapses).
      tempCDelayStartTime = millis(); // mark when we made the request to make sure we wait long enough before reading it.
    }

    sensor.readSensor(); //read pressure sensor
    pressure_abs = sensor.pressure();

    DateTime now = rtc.now(); //check RTC
    char dateTimeString[40];
    get_date_time_string(dateTimeString, now);

    //output readings to serial
    Serial.print(dateTimeString);
    Serial.print(",");
    Serial.print(pressure_abs);
    Serial.print(",");
    Serial.print(tempA);
    Serial.print(",");
    Serial.print(tempB);
    Serial.print(",");
    Serial.print(tempC);
    Serial.print(",");
    Serial.println(EC);

    //output readings to data file.
    File dataFile = SD.open(datalogFileName, FILE_WRITE);
    if (dataFile) {

      dataFile.print(dateTimeString);
      dataFile.print(",");
      dataFile.print(pressure_abs);
      dataFile.print(",");
      dataFile.print(tempA);
      dataFile.print(",");
      dataFile.print(tempB);
      dataFile.print(",");
      dataFile.print(tempC);
      dataFile.print(",");
      dataFile.println(EC);
      dataFile.close();

      }

  }

  // Tip: For a slower overall logging frequency, set the EC_SAMPLING_FREQUENCY variable rather than adding a delay (this will avoid the possibility of garbled ec sensor readings)

}

void get_numbered_filename(char* outStr, const char* filePrefix, const char* fileExtension) {

  // Make base filename
  sprintf(outStr, "%s000.%s", filePrefix, fileExtension);
  int namelength = strlen(outStr);
  if (namelength > 12) Serial.println("Error: filename too long. Shorten your filename to < 5 characters (12 chars total w number & file extension) !");

  // Keep incrementing the number part of filename until we reach an unused filename
  int i = 1;
  while (SD.exists(outStr)) {  // keep looping if filename already exists on card. [If the filename doesn't exist, the loop exits, so we found our first unused filename!]

    int hundreds = i / 100;
    outStr[namelength - 7] = '0' + hundreds;
    outStr[namelength - 6] = '0' + (i / 10) - (hundreds * 10);
    outStr[namelength - 5] = '0' + i % 10;
    i++;

  }

}
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

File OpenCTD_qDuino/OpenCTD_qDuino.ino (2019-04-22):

//Wire and MS5803_I2C libraries for communicating with the pressure sensor. 
#include <Wire.h>                                                                                
#include <SparkFun_MS5803_I2C.h> //CAN WE MAKE THIS LIBRARY SMALLER?

//EC Circuit uses software serial
#include <SoftwareSerial.h>     // For use by EC circuit.

//OneWire is used to get data from both temperature and conductivity sensors
#include <OneWire.h>  //CAN WE MAKE THIS LIBRARY SMALLER?

//DallasTemperature is used to query the temeprature sensors           
#include <DallasTemperature.h>   //CAN WE MAKE THIS LIBRARY SMALLER?

// For the SD card reader.
#include <SPI.h>               
#include <SD.h>

// For the Real-Time Clock
// #include <RTClib.h>

// Declare global variables.
float tempA;
float tempB;
float tempC;

float EC_float = 0;  // Electrical conductivity.

char EC_data[48];    // A 48 byte character array to hold incoming data from the conductivity circuit. 
char *EC;            // Character pointer for string parsing.

byte received_from_sensor = 0;  // How many characters have been received.
byte string_received = 0;       // Whether it received a string from the EC circuit.

SoftwareSerial ecSerial(8, 9);      // Define the SoftwareSerial port for conductivity.
OneWire oneWire(6);        // Define the OneWire port for temperature.
DallasTemperature sensors(&oneWire);  // Define DallasTemperature input based on OneWire.
MS5803 sensor(ADDRESS_HIGH);          // Define pressure sensor.

double pressure_abs; //define absolute pressure variable

// Starts it up.

void setup(void) {

  Serial.begin(9600);   // Set baud rate.
  ecSerial.begin(9600); // Set baud rate for conductivty circuit.

  pinMode(10, OUTPUT);  // Set data output pin for the SD card reader.
  
  // Test to see if the SD card reader is functioning.
  if (!SD.begin(4)) {
    Serial.println("Card failed");  // Log to serial monitor if SD card doesn't work.
    return; 
  }
  delay(500);  // Wait half a second before continuing.
  
  sensor.reset(); //reset pressure sensor 
  sensor.begin(); //initialize pressure sensor
  sensors.begin();  // Intialize the temperature sensors.
  
  delay(250);       // Wait a quarter second to continue.

  File dataFile = SD.open("datalog.txt", FILE_WRITE);
  if (dataFile) {
    dataFile.println("");
    dataFile.println("=== New Cast ===");
    dataFile.close();
  }
  else {

  }

}
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

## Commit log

2015-08-21 Minor code cleanup (Slightly risky)
    Mostly harmless stuff. And this...
    Serial is a singleton, which gets constructed exactly once, in headers somewhere. Since there can be no additional instances, I created a reference to it named monitorSerial. If that line isn't broke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
2015-08-21 Omitting Stale Measurements
    Extrapolating possible intent from that "string_received" global before, this patch only prints EC_data values if they were obtained during the current loop() iteration. Otherwise, "---" is logged in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
    .
    .
    Sidenote: ecSerial.readBytesUntil(13, ...) seems fairly safe. It only threatens incomplete reads if you underestimate the max chars per line - or if the device becomes unresponsive until the serial's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
    .
    .
    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
2015-10-13 Added 3D printer file
    [OpenCTDv4.stl]
2015-10-15 Just heaps of data
    Added all data files from the BlueHeron 2015-11 Research cruise on Lake
    Superior, including all raw and processed files pertaining to CTD Casts.
    Need to establish readme regarding this cruise for ease of access.
    [BH15-11_001-01_SternerB_001_CTD.xlsx, BH15-11_001-01_SternerB_001_CTD_Ascent.csv, BH15-11_001-01_SternerB_001_CTD_Descent.csv, BH15-11_003-02_WestMooring_CTD.x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]
2015-10-15 Cleaned up CSV files
    [BH15-11_001-01_SternerB_001_CTD_Ascent.csv, BH15-11_001-01_SternerB_001_CTD_Descent.csv, BH15-11_003-02_WestMooring_CTD_Ascent.csv, BH15-11_003-02_WestMooring_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]
2015-10-15 Fixed file name
    [BH15-11_001-01_SternerB_001_CTD.xlsx, BH15-11_001-01_SternerB_001_CTD_Ascent.csv, BH15-11_001-01_SternerB_001_CTD_Descent.csv, BH15-11_003-02_WestMooring_CTD.x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]
2015-10-16 Added calibration information.
2015-10-17 Added Sketchup Files
    [OpenCTDv4.skp]
2016-06-18 #HackTheOcean Marathon Session
    Code changes, STL fixes, upgrades, glory
    [OpenCTDv4.skp, OpenCTDv4.stl]
2016-06-18 Updated STL files
    [OpenCTDv4.skp, OpenCTDv4.stl]
2016-06-18 Fix STLs
    [OpenCTDv4.skp, OpenCTDv4.stl]
2016-06-18 Added two inch pipe plate
    [OpenCTD_2in.skp, OpenCTD_2in.stl]
2016-06-19 added servoflo to BOM
2016-06-21 Updated calibration instructions, almost done!
2016-07-20 Uploaded Data
    [thaler_test1_7_20_16.csv, thaler_test2_7_20_16.csv]
2016-07-20 Updated pressure test
    [thaler_test1_7_20_16.csv, thaler_test2_7_20_16.csv]
2017-01-17 Update README.md
    Fixed typos, added notes about sourcing, changed pressure sensor seating instructions
2017-03-30 Updated BoM
    Updated the bill of materials and made it more user friendly.
2017-03-30 Update README.md
    Added acrylic tube.
2017-04-05 Temperature
    Added links for Cave Pearl Project about temperature calibration.
2017-08-28 Fixed typos and added details to 3D Printed Parts
2017-09-22 Added support for pressure sensor tester
2017-09-22 added note about pressure sensor software
2017-09-22 Updated pressure test folder
    [thaler_test1_7_20_16.csv, thaler_test2_7_20_16.csv]
2019-04-22 house cleaning
    [OpenCTD_2in.skp, OpenCTD_2in.stl, OpenCTDv4.skp, OpenCTDv4.stl]
2019-06-29 Moved older CTD to retired folder
    [OpenCTD_2in.skp, OpenCTD_2in.stl, OpenCTDv4.skp, OpenCTDv4.stl]
2019-07-05 Added files and images
    [2-inch_PVC_NotchJig.stl, 2-inch_PVC_PaintCap_Bottom.stl, 2-inch_PVC_PaintCap_Top.stl, OpenCTD_Baseplate_M0.stl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]
2019-12-09 Update
    Excel template and standard baseplate
    [OpenCTD_Baseplate_M0.stl]
2020-10-12 Fix EC & Temp Sensor Timing Bug
    Fixes issue that caused EC sensor output to occasionally contain weird characters or miss line-endings. I found this happened when the serial data from the EC sensor happened to come in at the same t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
    Fix:
    1) I moved the temperature measurement steps so they only happen immediately after the EC sends a full measurement back.
    2) use the setWaitForConversion(false) mode in the Dallas Temperature Library so that it can request a temperature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
2020-10-12 Now it starts a new data log each time it is powered up
    Big Changes:
    1) Makes a new data log each time it is powered up rather than appending to the old one.
    2) Uses the CSV file format (Comma Separated Values) for easier use in programs like excel and others.
    3) First column contains the Date & Time with a space inbetween (I found Excel & Python parsed this date time format better)
    ^ This is easy to switch back (see the note in the get_date_time_string function)
    Improvements:
    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
2022-03-10 New Chassis
    [OpenCTD_ElectronicsChassis_M0.stl, OpenCTD_ElectronicsChassis_M0_Reinforced_Switch.stl]
2022-05-03 Create folder for Arduino Libraries
2022-05-03 Move EC calibration from standalone folder
2022-06-03 Added PCB File
2023-03-17 top-level project reogranization
    [2-inch_PVC_PaintCap_Bottom.stl, 2-inch_PVC_PaintCap_Top.stl, OpenCTD_Connector_M0.stl, OpenCTD_DataConversion_Template.xlsx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]
2023-05-04 Reorganize
    not all 3d print files are for the enclosure
    [2-inch_PVC_PaintCap_Bottom.stl, 2-inch_PVC_PaintCap_Top.stl, OpenCTD_Connector_M0.stl, OpenCTD_ElectronicsChassis_M0_Reinforced_Switch.stl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]
2023-06-12 Calibration protocol update
    complete rewrite of the calibration software for the sole purpose of getting a carriage return between each line.
2023-06-12 Revert "Calibration protocol update"
    This reverts commit 07e96f322140d102123a8a6c9b91f18167ef9273.
2023-06-13 Complete rewrite of Calibration Software
    Ground up rebuild to make it actually user friendly. Now has menu of commands, sets sample rate to zero, and has line breaks for data.
2023-06-13 Upgrades to calibration software
    added more descriptive command menu
2023-06-13 Cleaned up data template
    Everyone loves excel, right?
    [OpenCTD_DataConversion_Template.xlsx]
2023-06-14 Create OpenCTD_CalibrationDataManagement.pdf
    Added Calibration Guide
2023-06-20 Added temperature readings to calibration code
    Added temperature readings to calibration software
2023-06-27 Update 3D prints
    [2-inch_PVC_PaintCap_Bottom.stl, 2-inch_PVC_PaintCap_Top.stl, OpenCTD_14Bar_Baseplate.3mf, OpenCTD_Connector_M0.stl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]
2023-12-20 Updated New Manual
    [OpenCTD_DataConversion_Template.xlsx]
2024-04-10 update 3D printer files
    [OpenCTD_ElectronicsChassis_Bottom.3mf, OpenCTD_ElectronicsChassis_Top.3mf]
2024-04-10 added router jigs
    [RouterJigForHousing1.3mf, RouterJigForHousing2.3mf]
2024-04-10 add power management upgrade
2024-04-10 added new control board
    [kicad-openctd-B_Cu.gbr, kicad-openctd-B_Mask.gbr, kicad-openctd-B_Paste.gbr, kicad-openctd-B_Silkscreen.gbr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]
2024-08-16 EZO LED
    Added code to allow users to turn the Atlas EZO LED indicator light on or off to preserve power
    [OpenCTD_DataConversion_Template.xlsx]
2024-08-27 Added code to run the 5803-14ba pressure sensor in circuitpython
2026-06-17 Added Rev8 3D prints
    [2-inch_PVC_PaintCap_Bottom.stl, 2-inch_PVC_PaintCap_Top.stl, OpenCTD_14Bar_Baseplate.3mf, OpenCTD_Connector_M0.stl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]
2026-06-17 moved PCB files
    [kicad-openctd-B_Cu.gbr, kicad-openctd-B_Mask.gbr, kicad-openctd-B_Paste.gbr, kicad-openctd-B_Silkscreen.gbr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]
2026-06-18 Added 3 more files
    [Cap_Wrench.3mf, OpenCTD_Rev8_Baseplate_IMU.3mf, OpenCTD_Rev8_Baseplate_SF.3mf]
2026-06-18 Moved old CTDs to retired
    [OpenCTD_2in.skp, OpenCTD_2in.stl, OpenCTDv4.skp, OpenCTDv4.stl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]
2026-06-18 added PCB
2026-06-18 update gerbers
    [OpenCTD_Rev8_PCB.kicad_pcb]
2026-06-18 Added OfE_CPS
    [Ofe_CPS.kicad_pcb]
2026-06-18 Fix Calibration program to work with new temperature
